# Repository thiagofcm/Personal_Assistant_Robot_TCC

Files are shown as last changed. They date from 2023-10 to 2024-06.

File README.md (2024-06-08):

# Personal Assistant Robot - Bachelor's Thesis

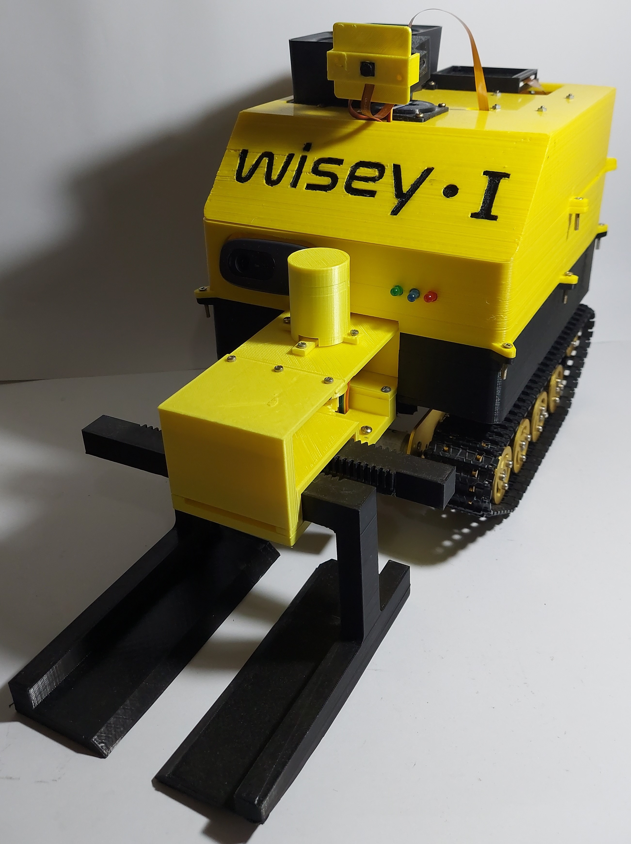
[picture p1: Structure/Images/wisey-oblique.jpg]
robot-oblique


# 1. Objective 
The main goal of this work is the development of an assistive robotic system capable of serving as an alternative for the care of elderly individuals with motor limitations. The robot will feature hardware and software resources related to artificial intelligence and computer vision applications to navigate through a domestic environment. Through voice commands, it will perform three tasks: recognize and deliver objects (Finder Mode), provide information and interact with users (Conversation Mode), and follow individuals (Follow Mode).

# 2. Methods

# 2.1 Development of MCUs firmwares:
- Development of Raspberry Pi 3 firmware, involving speech recognition and serial communication to send commands to the Maixduino MCU.
- Development of Maixduino firmware responsible for object and face detection, and reception of commands and data from the Raspberry Pi.
- Development of STM32 firmware, responsible for controlling motors and the ultrasonic sensor, as well as receiving commands and data from the Maixduino MCU.

# 2.2 Development of a PCB:
A professional PCB was designed on KiCad to ensure robust hardware-level functionality

# 2.3 Development of a robust structure:
- The robot's structure consists of a rover track belt connected to each motor, an aluminum chassis, and an external 3D structure.

# 3. Results

# 3.1 Software Design: 
Internally, the robot's functionallity is based on 3 embedded firmwares in 3 MCUs: 

- Raspberry Pi 3: This firmware responsible for Wi-Fi connectivity, processing audio data via the Google Speech-to-Text API, and transmitting data via UART to the Maixduino MCU. Basically, the Raspberry Pi will listen to voice commands and look for specific keywords, like "follow" or "bring me". Depending on which word/expression was detected, the Raspberry will send a UART message to Maixduino defining which AI it has to run
- Maixduino Sipeed: This MCU houses the neural network, camera, and embedded machine learning models. More especifically, this Maixduino's firmware runs AI models for object and face recognition under UART commands from the Raspberry Pi, and transmit targets coordinates to a STM32 MCU. 
- STM32F41106CCEU6:  This MCU is in charge of receive UART data from the Maixduino MCU and apply PWM signals to control the robot's position. The SMT32's firmware also controls an ultrassonic sensor and a buzzer that is enable when an obstacle is detected under 20cm

The image below shows a diagram illustrating the functionality, peripherals, and the relationship established between the MCUs.

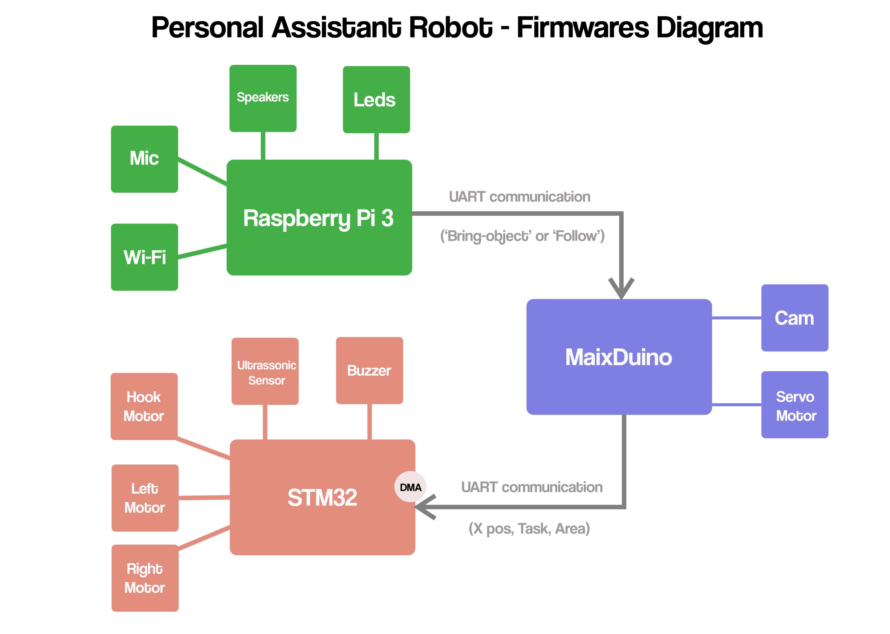
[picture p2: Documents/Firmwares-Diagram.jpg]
SOFTWARE_DESIGN


# 3.2 PCB Development: 
A Printed Circuit Board (PCB) compatible with all the hardware resources used in the system, from MCUs to sensors, motors, LEDs, etc., was designed using the KiCad software. After being designed, the board was manufactured by JLC PCB. Below are images of the board layers as well as the board already fabricated and assembled. The files for reproduction and more information about this part of the project can be found in the PCB folder.

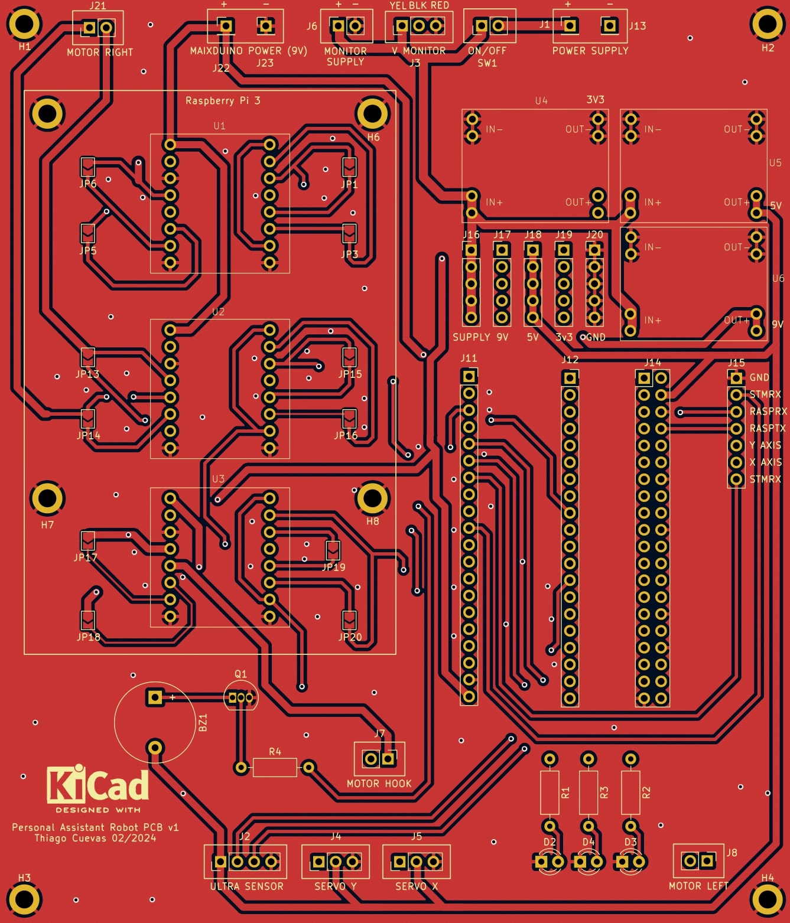
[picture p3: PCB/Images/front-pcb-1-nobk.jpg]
PCB_FRONT

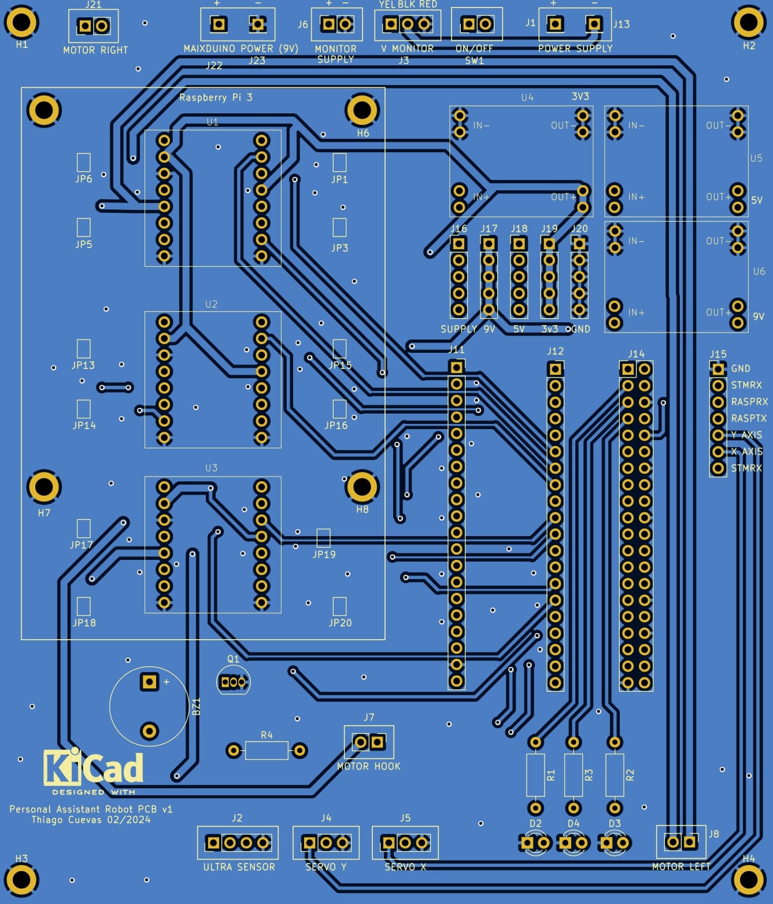
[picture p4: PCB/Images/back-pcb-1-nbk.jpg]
PCB_BACK

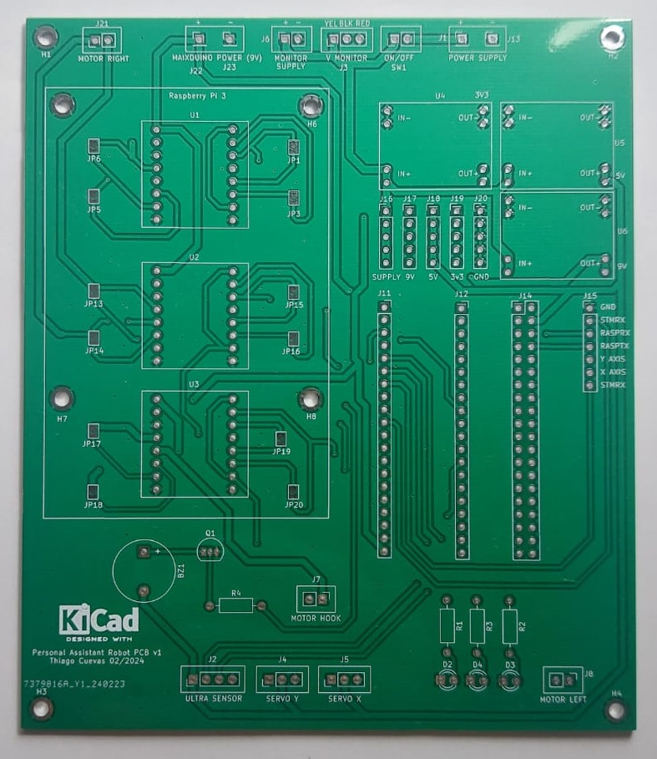
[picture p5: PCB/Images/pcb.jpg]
PCB_MANUFACTURED

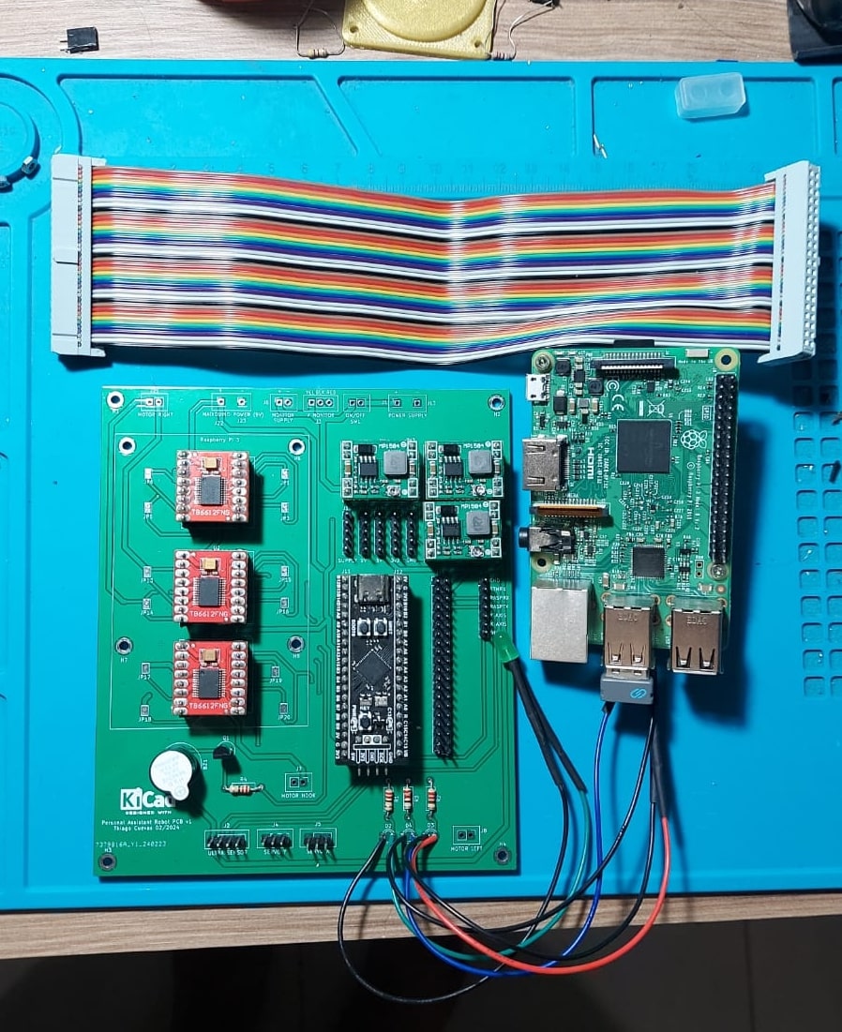
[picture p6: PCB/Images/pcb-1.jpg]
PCB_MOUNTED_1

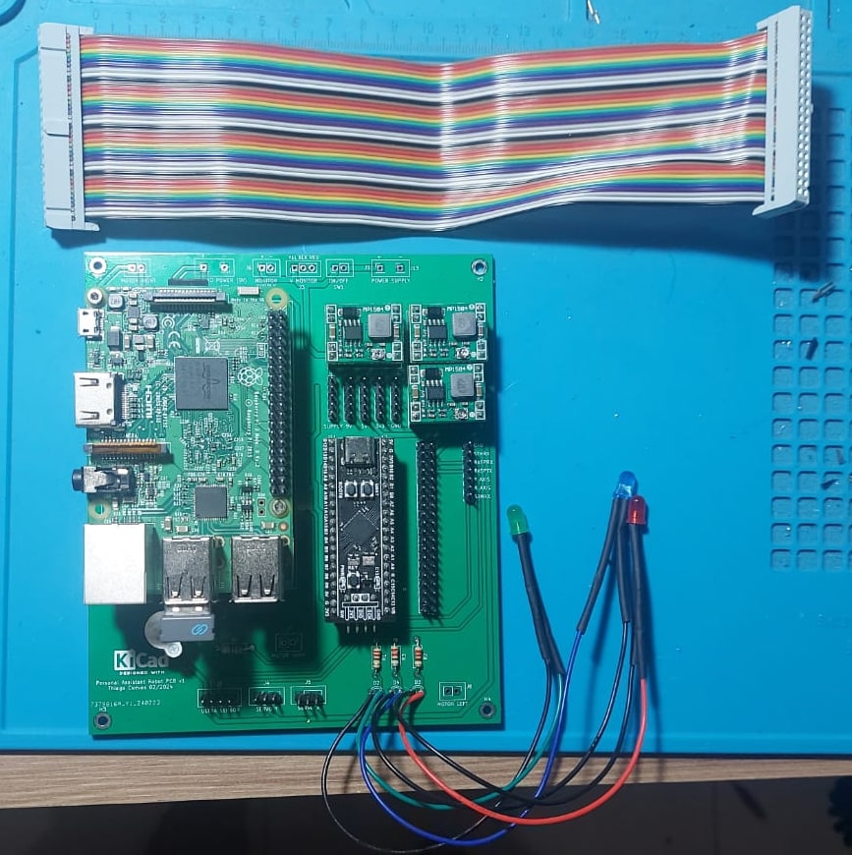
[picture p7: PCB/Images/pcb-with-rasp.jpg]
PCB_MOUNTED_2


# 3.3 Structure Design
A modular structure was designed using the 3D modeling software Fusion 360 and was subsequently manufactured using 3D printing technology. All parts were designed to be compatible with the physical components of the system, as well as adapted to enhance the system's performance. The .SLT, .F3D files, and more images can be found in the Structure folder.

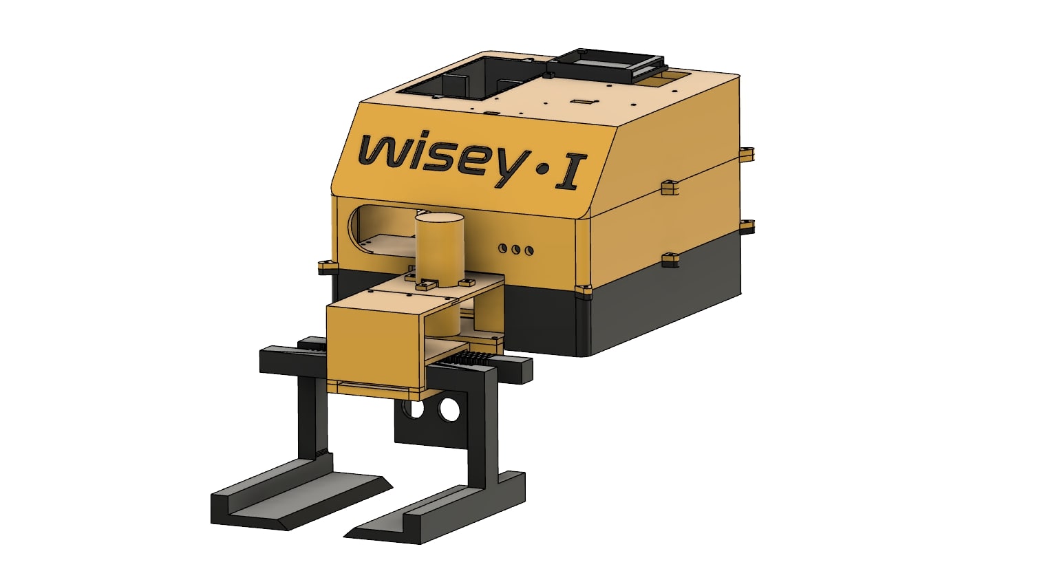
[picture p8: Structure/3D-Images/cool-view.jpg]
3D-VIEW

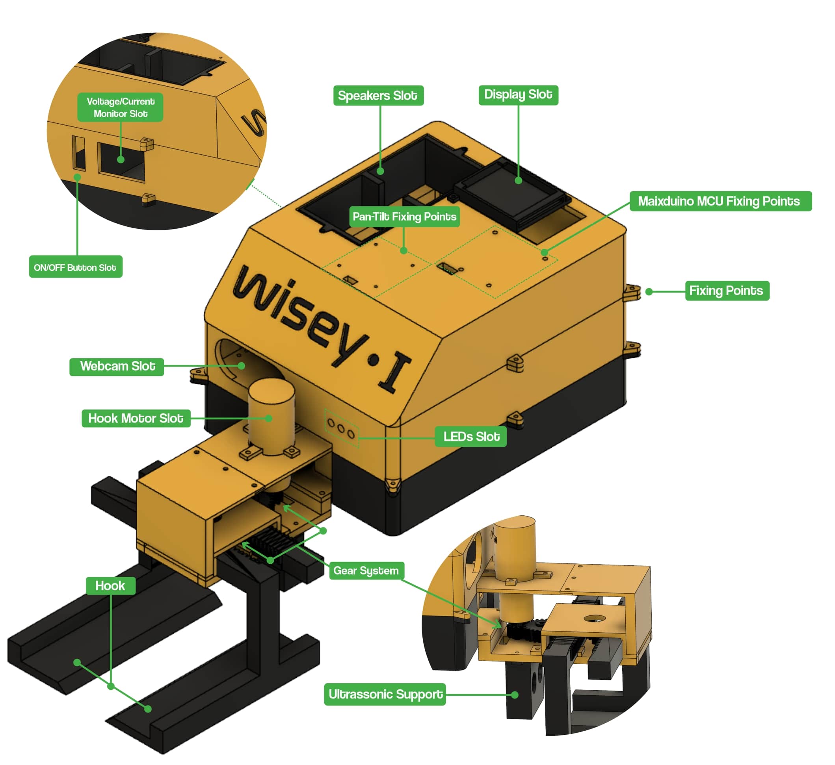
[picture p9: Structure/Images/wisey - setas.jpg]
3D-VIEW_WITH_SETAS


# 4. Robot Images:
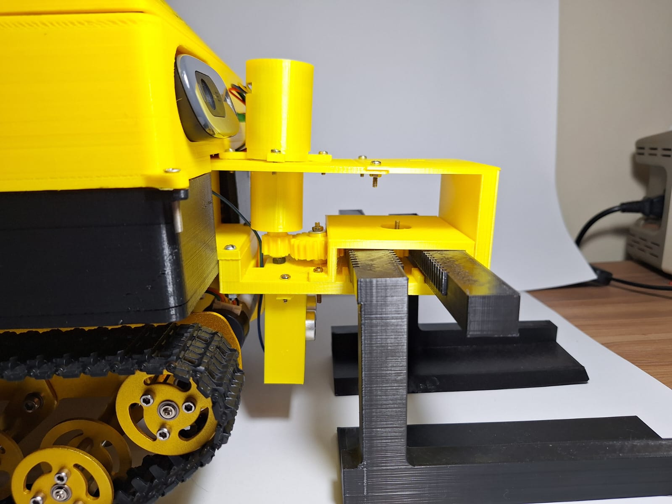
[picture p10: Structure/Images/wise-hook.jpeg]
Personal_Assistant_Robot1


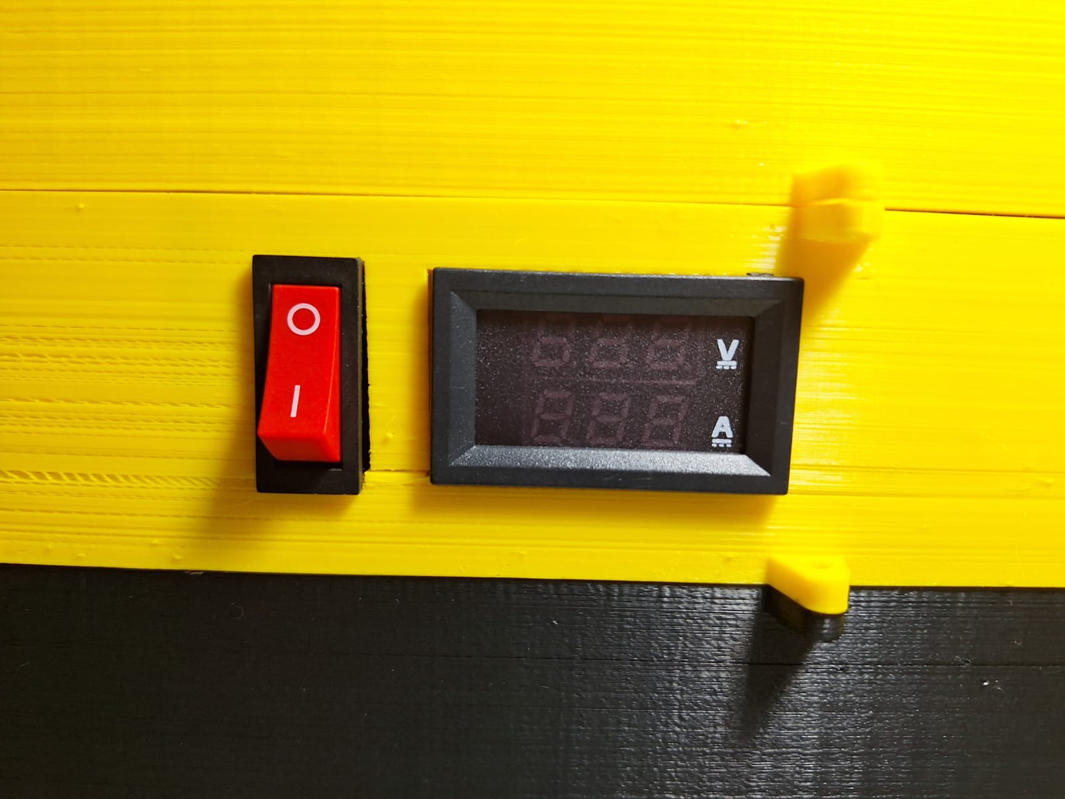
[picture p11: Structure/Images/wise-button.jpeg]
Personal_Assistant_Robot2


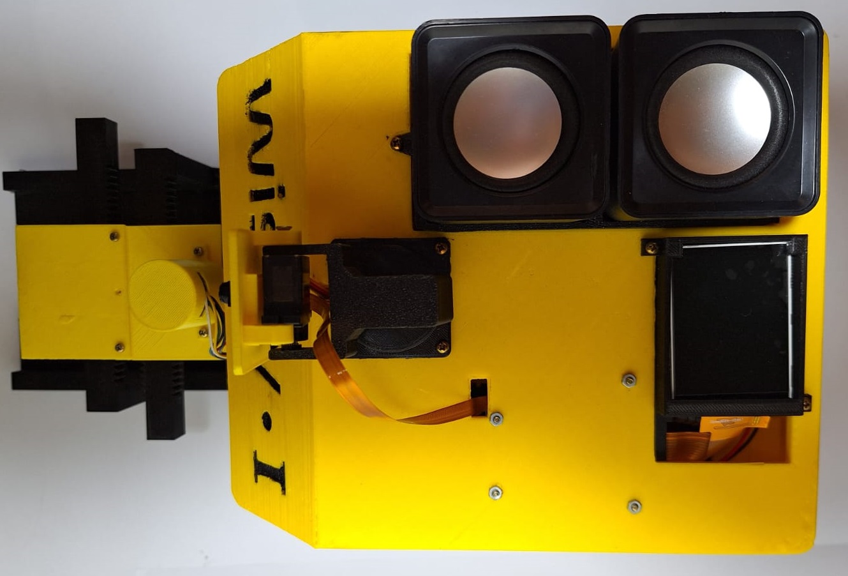
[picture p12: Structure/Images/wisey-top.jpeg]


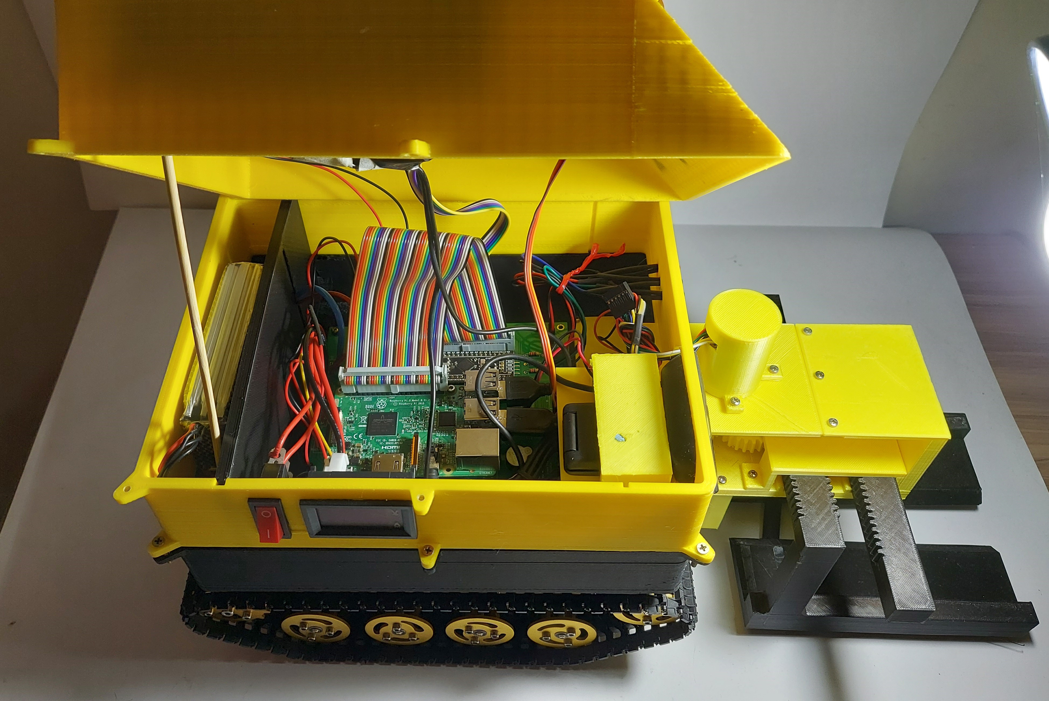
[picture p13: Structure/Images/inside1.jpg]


In the Development Checkpoints folder, you can find the entire development process of the project, including problems, solutions, challenges, tests, failures, and successes. I found it important to document this entire process so that if anyone is interested in reproducing and improving the project, they have references.

# 5. Functionallity

The images below ilustrate the current funcionality of the robot:

Follow Mode:

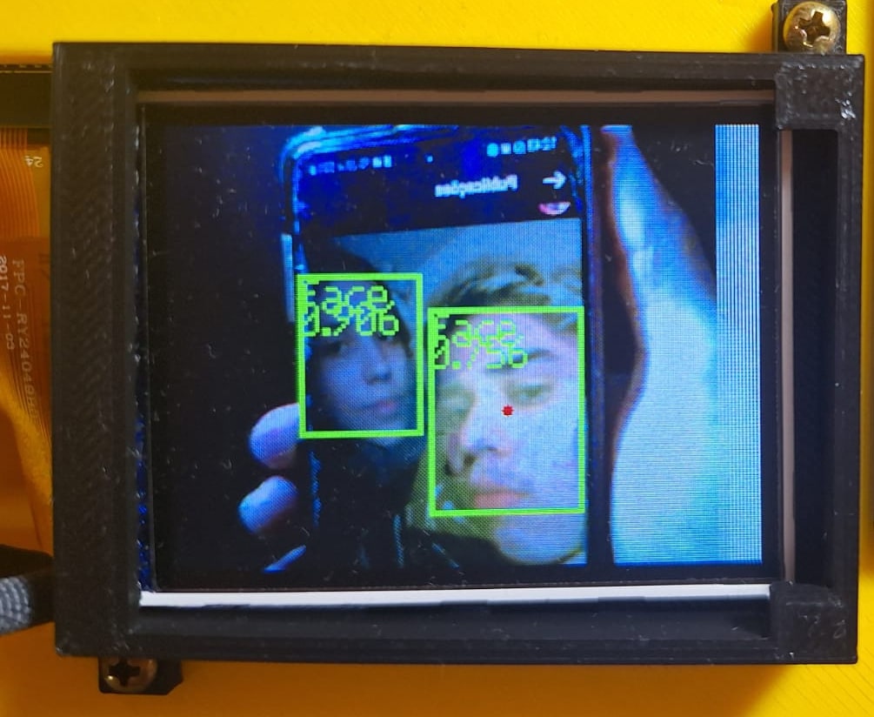
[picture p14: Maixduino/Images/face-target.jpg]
face_target


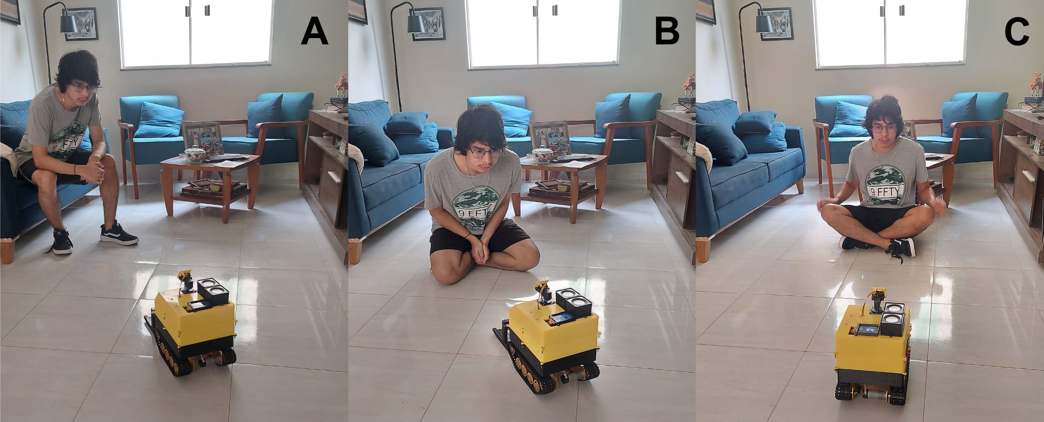
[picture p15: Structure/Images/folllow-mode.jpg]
follow-test


Finder Mode:
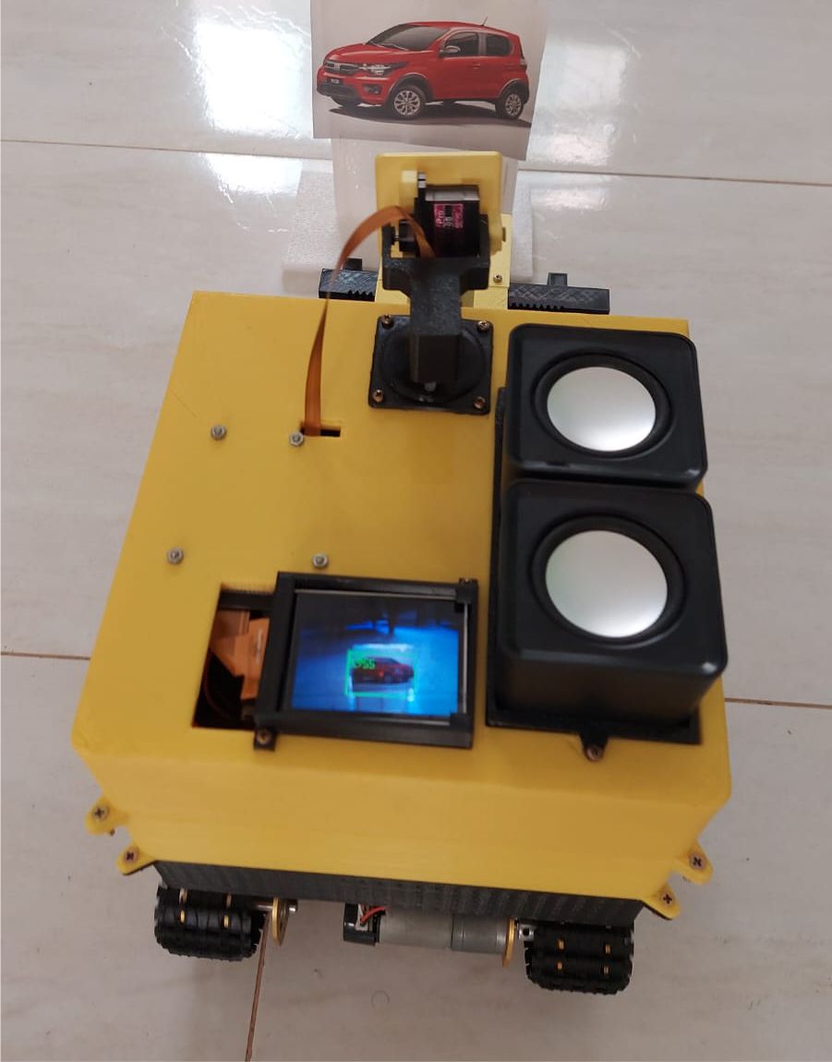
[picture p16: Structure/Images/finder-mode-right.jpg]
finder-test-right


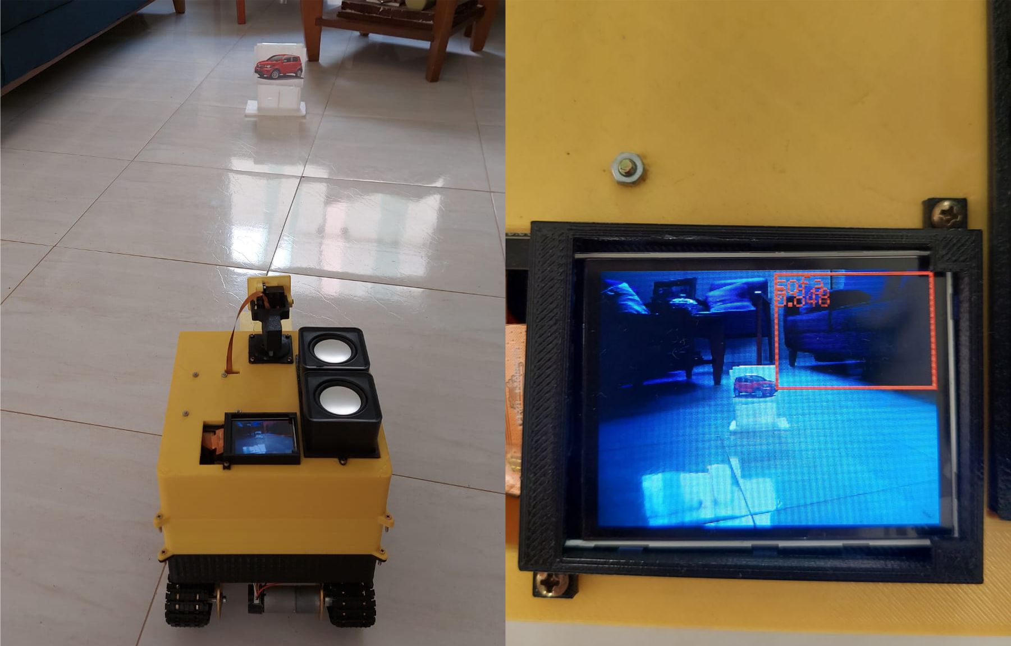
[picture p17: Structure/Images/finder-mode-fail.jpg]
finder-test-fail


# 6. Demonstration Video:

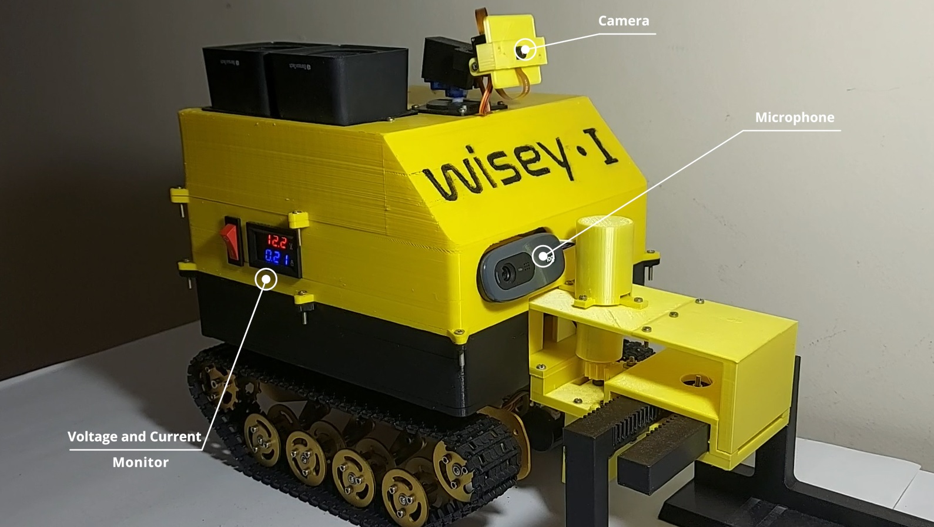
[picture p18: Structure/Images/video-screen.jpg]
video-screen


A demonstration video of the robot in operation is available at the following link: https://youtu.be/cWnuLTotcqo?si=knrNkCdaKpj5jtFy

# 7. References
The robot is a rover based on the project below:
https://github.com/SaralTayal123/Object-Finding-Rover/tree/master

Contact:
Email: thiagof1503@gmail.com
Linkedin: https://www.linkedin.com/in/thiago-cuevas/

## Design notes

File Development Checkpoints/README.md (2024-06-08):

# Updates and checkpoints:

01/08/23: Basic Hardware and Software Tests Stage - Motor Control tests.

11/08/23: Basic Hardware and Software Tests Stage - Ultrasonic sensor tests.

20/08/23: Basic Hardware and Software Tests Stage - Motor Control and Ultrasonic sensor Integration.

02/09/23: Basic Hardware and Software Tests Stage - Temporary PCB added to the circuit.

01/10/23: Basic Hardware and Software Tests Stage - The robot is now capable of moving through the environment and avoiding obstacles using the ultrasonic sensor. 

20/12/23: Writing and formalization of the preliminary project to be submitted to the evaluation committee of the Electrical and Computer Engineering Department.

07/01/24: Finish of the preliminary project (Documents/Projeto__TCC__Thiago_Cuevas.pdf).

12/01/24: Development of the speech recognition and voice assistant firmware on Rasbperry Pi 3 (Rasp/scr). 

16/01/24: Development of a UART communication firmware test between Rasp and Maixduino.

15/01/24: Development of the tracking objects firmware on Maixduino. A servo motor is already capable of follow the movement of an object.

20/01/24: Voice assistant running with an ChatGPT API that answers questions based on OpenAI database.

22/01/24: UART communication between Rasp and Maixduino done and already capable of switch between two different AI models (face recognition, to follow people, and object detection, to deliver objects).

23/01/24: Looking for complete and make improvements in the maixduino switching_models and voice_assistant code. Some problems include:
- The voice assistant still listening during an object or face detection task, which it's annoying because the assistant tries to listen and understand what he is not supposed to listen or understand.
- The Object recognition model needs to track and get the relative position of the object. The code at this point already satisfies this requirement, but without any filter. As the user asks for an especific object, the firmware has to understand and apply an filter to track the right object.
- The Face recognition model needs to track and get the relative position of a face, and also estimate a distance based on the area of the rectangle draw around a recognized face. This feature is not complete.

24/01/24: Looking for make improvements in the IA models. Updates:
- Maixduino is running a Switching models code able to change between the object detection and face detection model by serial commands from the Raspberry Pi.
- Maixduino display a message "waiting command" when it is awaiting for a voice/serial command by the user and the Raspberry Pi.

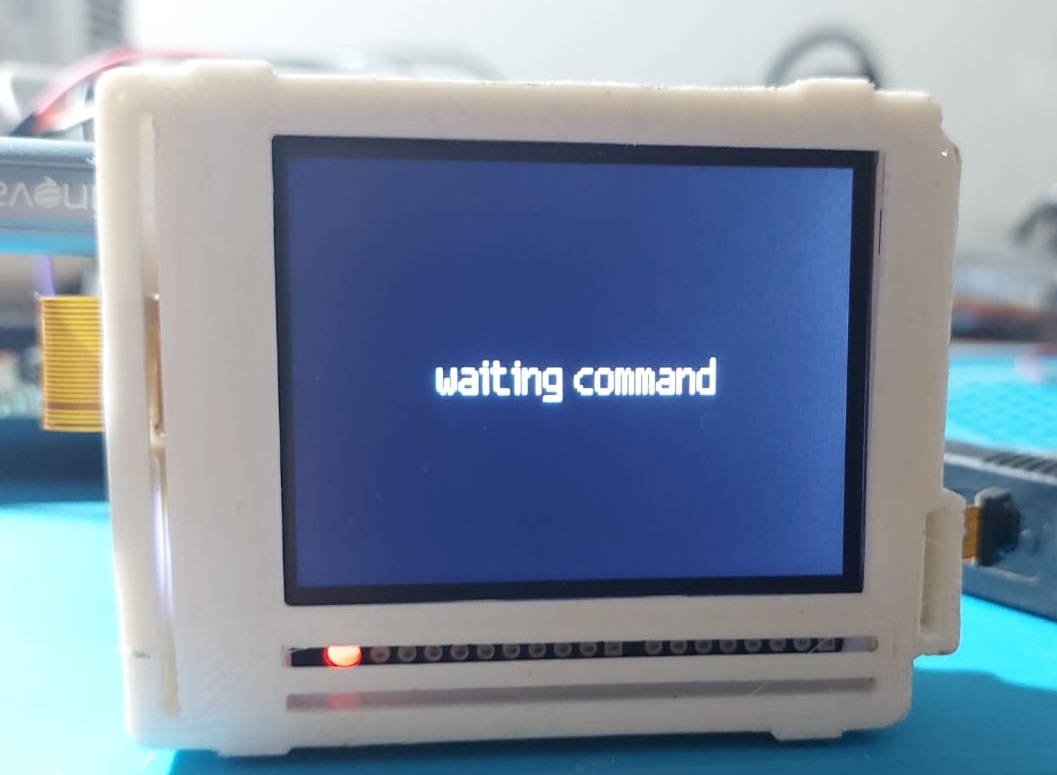
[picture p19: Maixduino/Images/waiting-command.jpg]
image_waiting_command


- Object detection function now gets the relative position only of the objects required by the user. In the example below, the object required was a car, so the rectangle red and the red circle in the center of the object represents that the model understand that is the object that has to be tracked. 

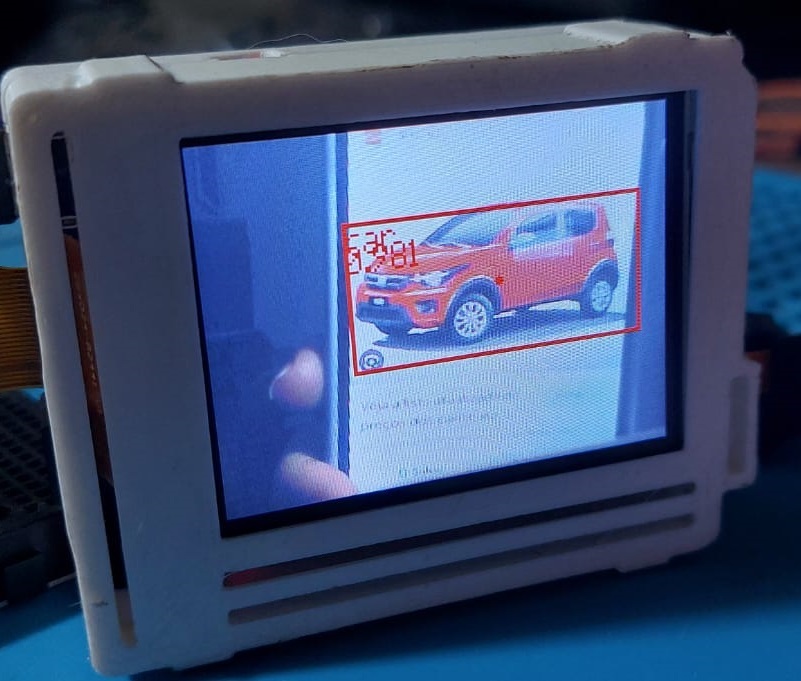
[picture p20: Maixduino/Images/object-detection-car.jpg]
image_car_object_detection


In other hand, the image of a dog, that's not a car is sourrounded by a green rectangle without any circle in the center, representing that despite recognized, the object is not being tracked.

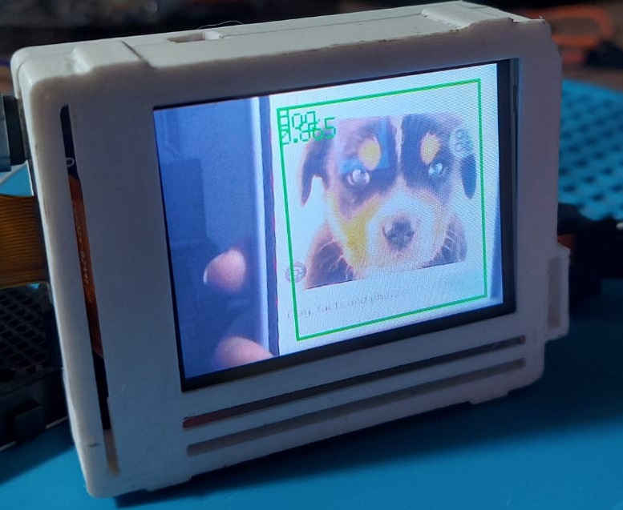
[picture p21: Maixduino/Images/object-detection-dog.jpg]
image_dog_object_detection


- Face detection function now gets the relative position of faces but just one at time. Seems like when more than one face is captured by the camera, the program doesnt know exactly wich face to track. 

25/01/24: Improvements in the Face Detection model done. Updates:
- The Face Detection model is now able to identify the face with largest area and draw a circle in the center of the rectangle area around the face. This circle is used to track de coordinates of the face's position.

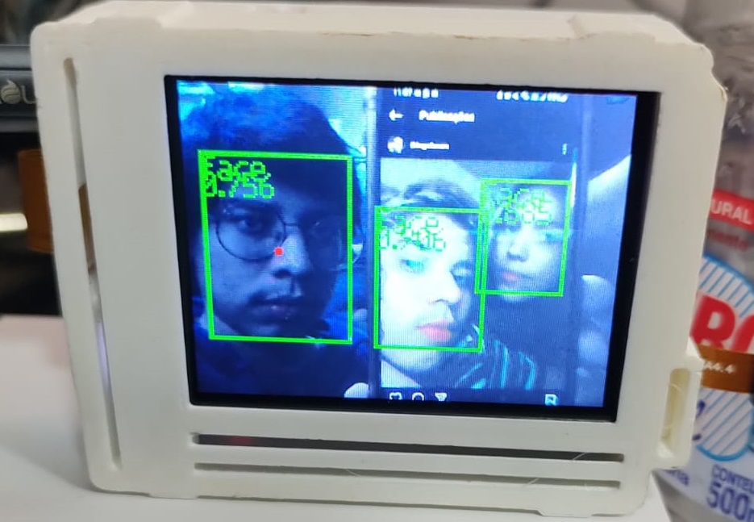
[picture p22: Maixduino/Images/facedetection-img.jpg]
faces_recognition


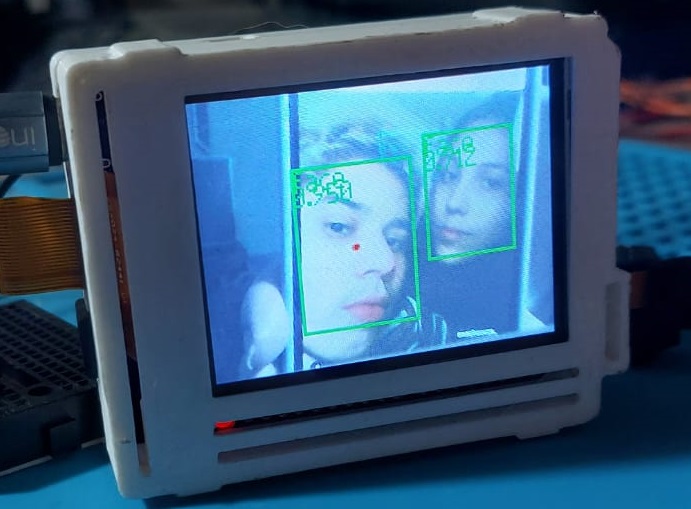
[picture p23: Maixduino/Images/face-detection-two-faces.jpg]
faces_recognition_2


29/01/24: A 3D Pan Tilt has been printed and added to see the servo tracking control. Updates:
- The tilt can follow the face with the biggest area. 
- Face detection firmware now gets the x and y relative position and send it via UART to the STM32 (UART seems to be easier to control than I2C protocol).
- The plan is make the STM32 MCU receive data in the format (x,y,area). I am trying to use the Direct Memory Access (DMA) to receive the data in order to significantly reduce the CPU load. However, I still don't know why, but the STM32 is receveing just one byte of the whole frame data from the Maixduino. Example: If I send (23,53,5432), the STM32 is able to fill one or two positions of the buffer, like '(' and sometimes '(' and '2'. I tested this STM32 firmware trying to receive data from the Raspberry Pi and it worked, but with Maixduino did not.

tracking_faces

01/01/24: The STM32 is now receiving the complete coordinates data from Maixduino, in the format (x,y,area) and using DMA. Updates:
- A new microphone from Logitech Webcam was added. Now, the voice recognition is more accurate and the system can listen commands in a larger distance.

02/02/24: Based on the x coordinate received by the Maixduino, the STM32 is now able to adjusts the PWM signal sent to the motors and make movements like turn to the right, left, and stop ensuring the robot maintains its position consistently in front of the object or face. 
- I still need to add a function to handle the received area data and adjust a threshold parameter to maintain an optimal distance between the object/face and the robot. However, to guarantee accurate modifications and calibrations in this implementation, it is necessary to have an autonomous system and structure already working, one that does not depend on USB supply. 
 
motor-tracking-objects

04/01/24: I developed a block diagram of the system workflow (Documents/Personal_Assistant_Diagram) to facilitate software and hardware design and development.  

07/02/24: I started the schematic of the PCB on KiCad. Software Updates:
- I made some improvements in the ST code. Now the motors stop and a buzzer is activated when an object or obstacle is within a range of 15cm of the robot.
- I added some LEDs to the Rasp Circuit. The green LED turns on when the system is initialized and ready to receive commands. The blue LED turns on when the wake-word is detected, and the red LED represents when the robot is busy on a task.
- These improvements are changes that I had already in mind since the beginning of the implementation, that I was just leaving for the end. However, the PCB design requires that all components and pinouts be counted.

27/02/24: I finished the PCB design on KiCad and have already ordered it on JLCPCB.
- I suppose to receive the PCB by mid or end of march.
- I modeled the 3D Structure on Fusion 360, and now I'm waiting to have all parts printed.

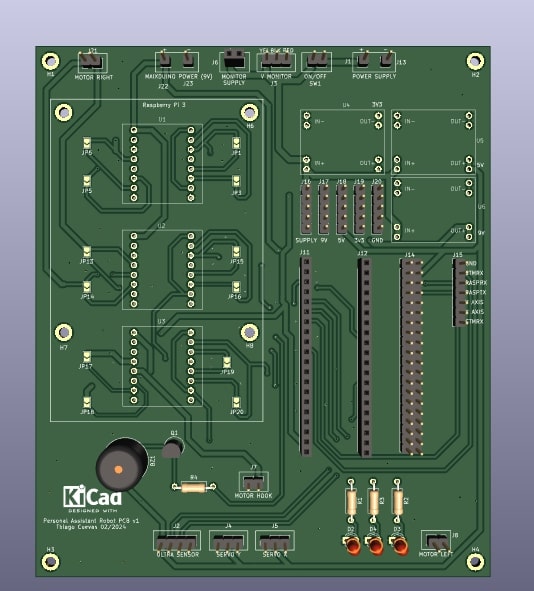
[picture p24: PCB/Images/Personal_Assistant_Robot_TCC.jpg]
PCB


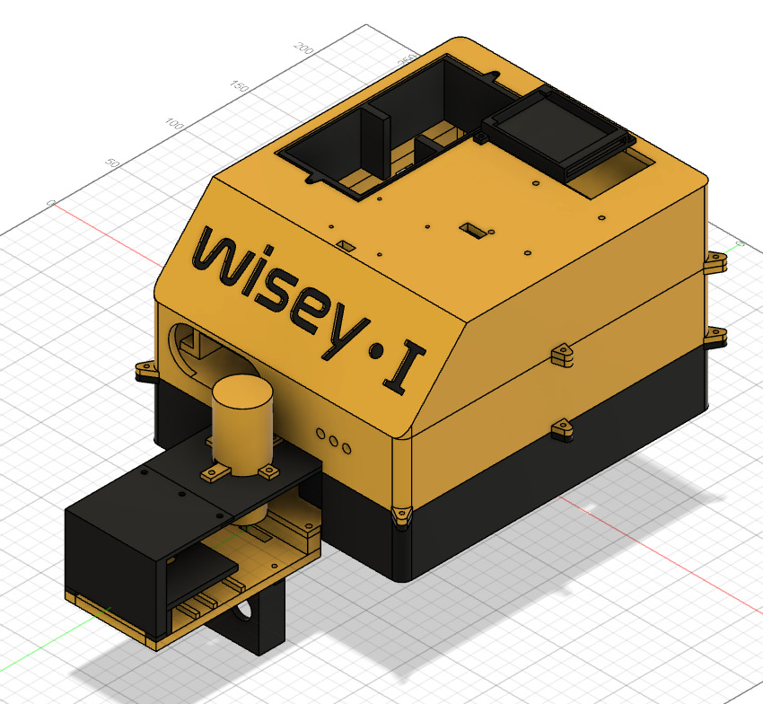
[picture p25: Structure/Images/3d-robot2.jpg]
3D_Structure


20/03/24: After nearly a month of anticipation, both the PCB and the 3D printed structure have finally arrived! :)

pcb-done

- I am currently in the process of soldering the components onto the PCB, meticulously testing each one before integrating them into the entire system. 

pcb-wout-rasp

- The 3D structure fits flawlessly and looks quite impressive.

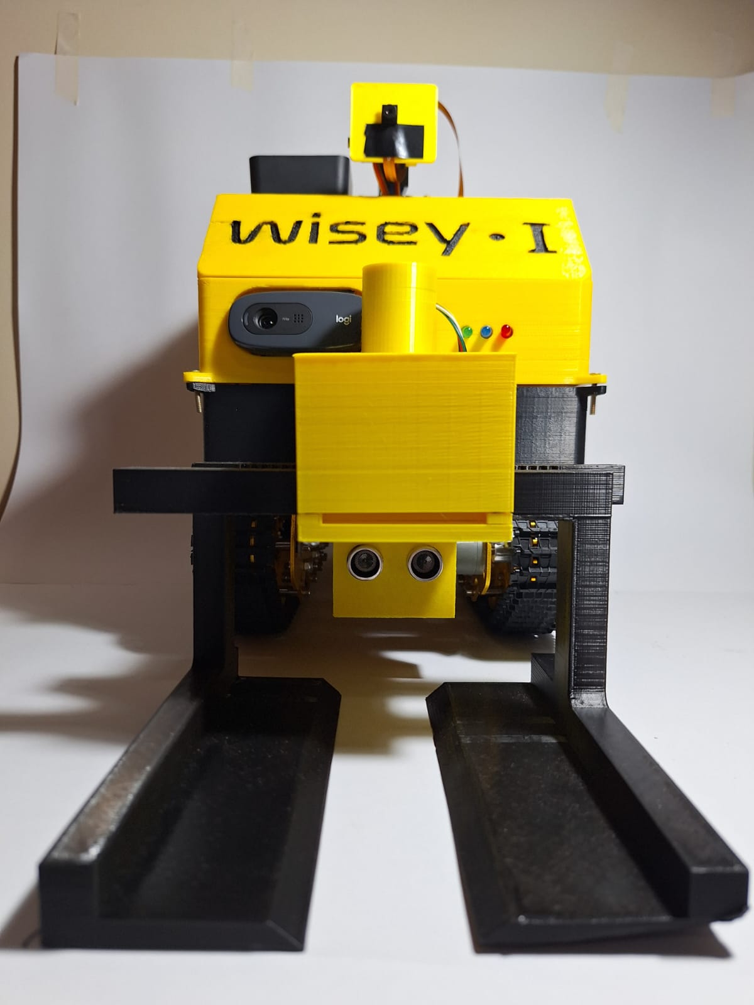
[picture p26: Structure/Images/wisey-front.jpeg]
robot-oblique


- Simultaneously, progress is being made on the written aspect of the project.

12/04/24: The PCB worked very well, and tests to verify the system functionality were conducted. 
- The system successfully interacted with the user, maintaining a fluent and cohesive conversation. 
- The robot also exhibited commendable performance in detecting and tracking users, although it encountered limitations in perceiving and capturing objects.
- Given that the detection model has a restricted list of recognizable objects, with not all of them being domestic items, an adapted structure with a picture of the object was devised to enhance the recognition of specific items.
- It was noted that the model is capable of recognizing objects at close range, possibly due to the camera's low resolution in this dimension.
- Also, the gripper system did not function as expected, likely due to insufficient motor torque and less effective gear system coupling. Despite this, the robot managed to detect objects under specific conditions and move towards them.
- The written part of the project has been done, and after be reviewd by the Faculty, will be available in the Documents directory.
- A video showing all the skills of the robot is under development, and will be available on Youtube.

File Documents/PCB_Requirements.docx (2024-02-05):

Projeto PCB – Personal Assistant Robot

Levantamento de Materiais e Componentes:

- MOTORES:

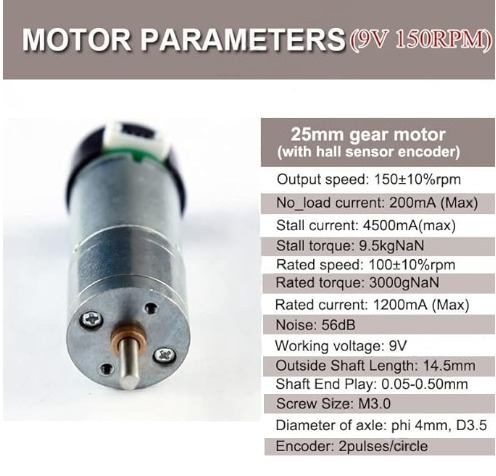
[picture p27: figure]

- Supostamente o motor que estou usando é:

Porém, estou em dúvida pois o modelo de 6V também existe. Medi com o multímetro a tensão que está chegando da ponte H até eles. Considerando a fonte de 12V, a tensão máxima que chega aos motores é de 6,2V. Segundo a imagem acima a corrente nominal é de 1.2A. Como saber qual motor é o meu? E O que aconteceria se alimentar com 3.0A?

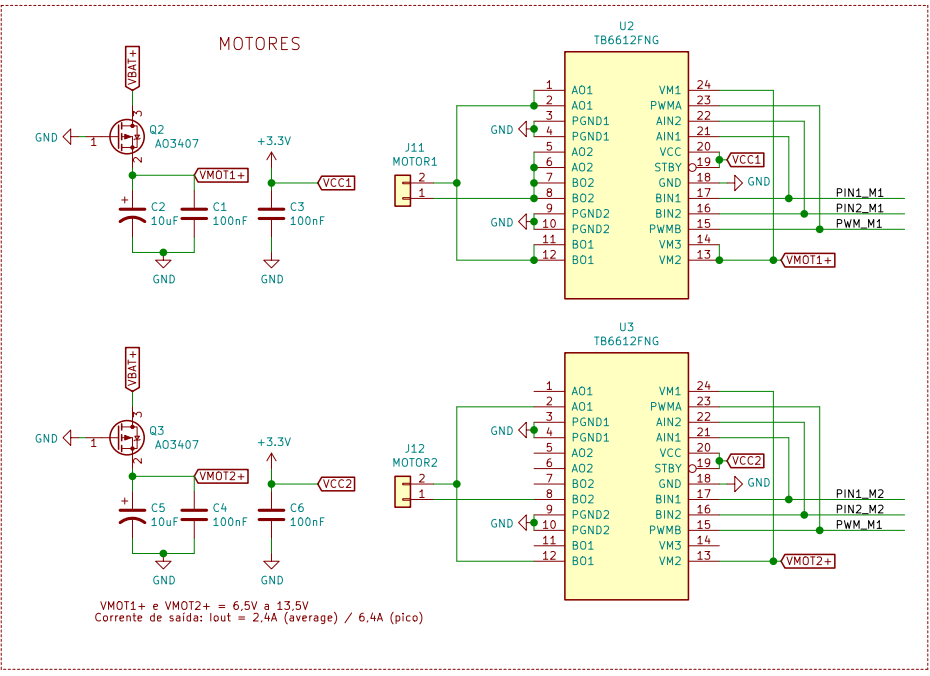
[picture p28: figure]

- Quanto ao controle dos motores, observando o projeto do Lukas, vi que ele usou dois chips TB6612FNG. Cada chip desses possui dois canais para controlar dois motores, mas Lukas usou os dois canais para o mesmo motor. O objetivo foi obter mais corrente para cada um dos motores, uma vez que cada canal fornece até 1,5A, tendo ao final, 3,0A para cada motor.

- A pinagem do TB6612FNG está detalhada no datasheet, é de fácil compreensão. Tenho algumas dúvidas sobre o circuito de alimentação dos motores (VMOT1+ e VMOT2+).

- REGULADORES DE TENSÃO:

A tensão que chega das baterias deve ser regulada para a operação de outros componentes que funcionam com tensão menor. Dessa forma, são necessárias tensões na placa de 6 a 12V, 5V e 3V3.

- Componentes alimentados por 6 as 12V:

x1 Maixduino MCU (via DC Connector)

- Componentes alimentados por 5V:

x1 Servo motor para controle do posicionamento da câmera no eixo Y.

x1 Sensor Ultrassônico.

x1 Raspberry PI 3 (pinos)

x1 Motor DC para controlar HOOK

- Componentes alimentados por 3v3:

x1 STM32F411CEU6

x3 LED’s

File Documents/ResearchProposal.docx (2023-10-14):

Proposta de Trabalho de Conclusão de Curso – Thiago Fernando Cuevas Mestanza

Título: Robô Assistente Pessoal Inteligente

Objetivo: Construir um robô assistente pessoal inteligente capaz de receber comandos por voz e executar tarefas simples como: seguir uma determinada pessoa (Follow Mode), trazer objetos (Find object Mode) e dar informações* (Info Mode)

Assuntos abrangidos: Robótica, Computação Visual, Machine Learning, Eletrônica, Sistemas Embarcados.

Referência direta:

https://www.instructables.com/Object-Finding-Personal-Assistant-Robot-Ft-Raspber/

https://github.com/SaralTayal123/Object-Finding-Rover/tree/master

https://youtu.be/aso3N4YiCAQ

Analise inicial de requisitos, o robô deve possuir:

- Uma estrutura similar a um chassi de carro – TANK SN2500

- Computador – Raspberry PI 3

- Motor Driver – MCU STM32

- Dispositivo com Rede Neural/ Machine Learning Embarcado – Kendryte K210

- Webcam c microfone- xxxxxxxx

- Sensor Ultrassônico - HC SR04

- Acabamento em impressão 3D

- Wi-Fi Driver – MCU ESP32*

- Saída de áudio*

Funcionamento:

A Raspberry PI 3 gerenciaria todas as atividades realizadas pelo robô, sendo ela a responsável por enviar as informações necessárias para os demais drivers e dispositivos, como a STM32, Sipeed e ESP32. Essa segmentação de atividades não sobrecarrega a capacidade de processamento da Raspberry, não compromete outras aplicações do computador e desenvolve as habilidades do estudante.

Nessa perspectiva, A STM32 funcionaria apenas como interface/Driver dos motores, enviando e recebendo informações da Rasp via I2C,RS-232 ou SPI.

O intuito é fazer o K210 funcionar da mesma forma, como uma rede neural a parte, encarregada de fazer o reconhecimento facial e de objetos por Machine Learning, interpretando a imagem obtida pela câmera, além de ser o sistema receptor de comandos de voz.

O Sensor Ultrassônico serviria como um medidor de distância, sendo utilizado somente quando acionado o modo “Find object”. Após um objeto ser encontrado, é ele que mede a distância ideal para acionar o sistema de garras e manter o objeto preso ao robô.

A ESP32 funcionaria como um modulo Wi-Fi capaz de gerenciar o trafego de informações e manter o robô conectado à internet e consequentemente disponível para dar informações sobre clima, localização, data e hora ao usuário através de uma saída de áudio. *

Bibliotecas necessárias:

Reconhecimento de voz

Reconhecimento facial

Reconhecimento de objetos

Principais dificuldades/duvidas:

Com o uso do Kendryte 210, uma câmera webcam não será mais necessária?

O Kendryte consegue reconhecer comandos de voz além do Wake-Word?

Como fazer a interface do Kendryte com o a Rasp?

Se não usarmos Kendryte, que outra opção temos para processamento de imagem?

Todas as bibliotecas necessárias rodam no mesmo MCU?

Outras Referências:

Tank Chassi SN2500 Guide: https://www.makerbuying.com/18100

Wake-Word K210: https://www.youtube.com/watch?v=zJmjSP2nwj0

Biblioteca SnowBoy para reconhecimento de voz com webcam e rasp: https://pimylifeup.com/raspberry-pi-snowboy/

Controle de Motor DC com Rasp e L298N Driver: https://www.youtube.com/watch?v=2bganVdLg5Q

Rasp e Sensor HCSR04: https://www.youtube.com/watch?v=_7drIUmC8Zo

Getting Started with Rasp: https://projects.raspberrypi.org/en/projects/raspberry-pi-getting-started/

Interface STM32 with Raspberry PI via i2c: https://www.youtube.com/watch?v=8SisMjqqgmc

Forum talk about Interface STM32 with Raspberry PI: https://forums.raspberrypi.com/viewtopic.php?t=213305

Maix BIT – Alternativa: https://blog.arduinoomega.com/maix-bit-embarcado-de-baixo-custo-com-ia/

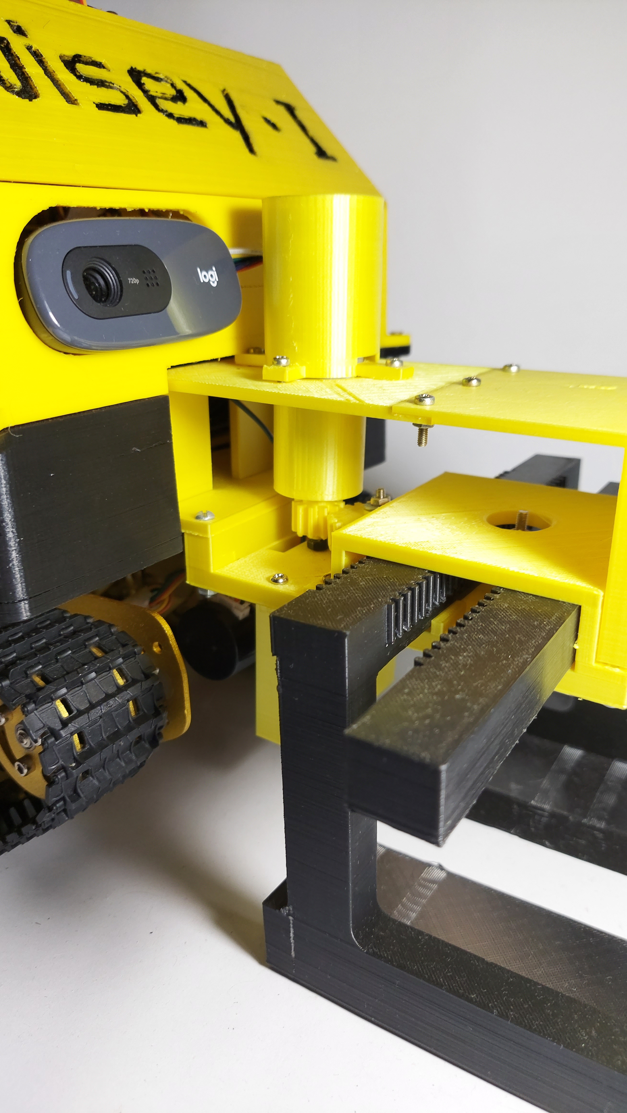
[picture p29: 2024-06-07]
Structure/Images/hook1.jpg

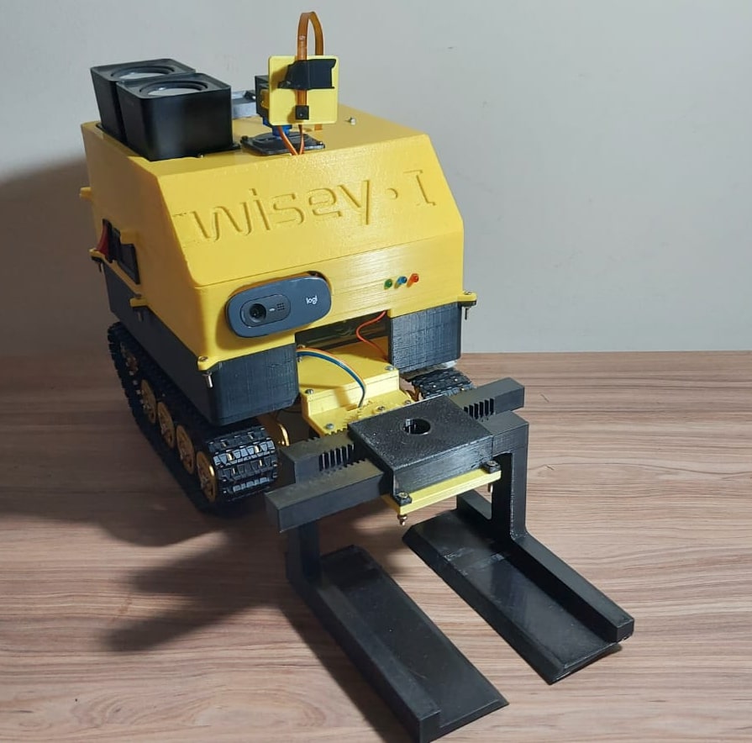
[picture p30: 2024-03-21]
Structure/Images/oblique.jpg

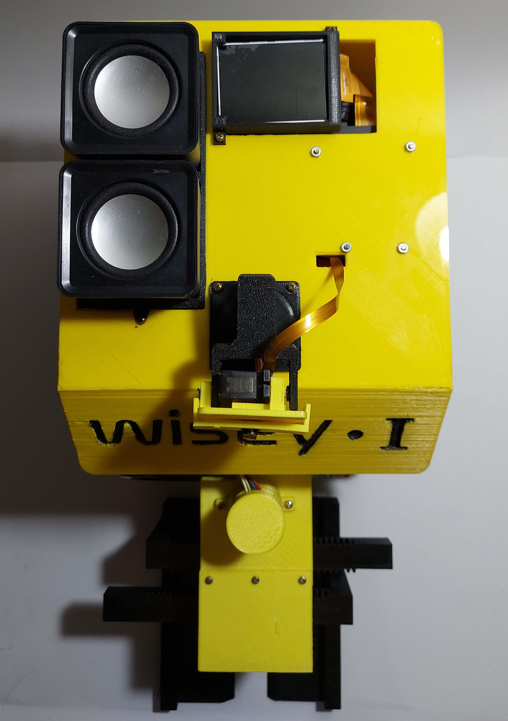
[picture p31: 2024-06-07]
Structure/Images/wisey-topv2.jpg

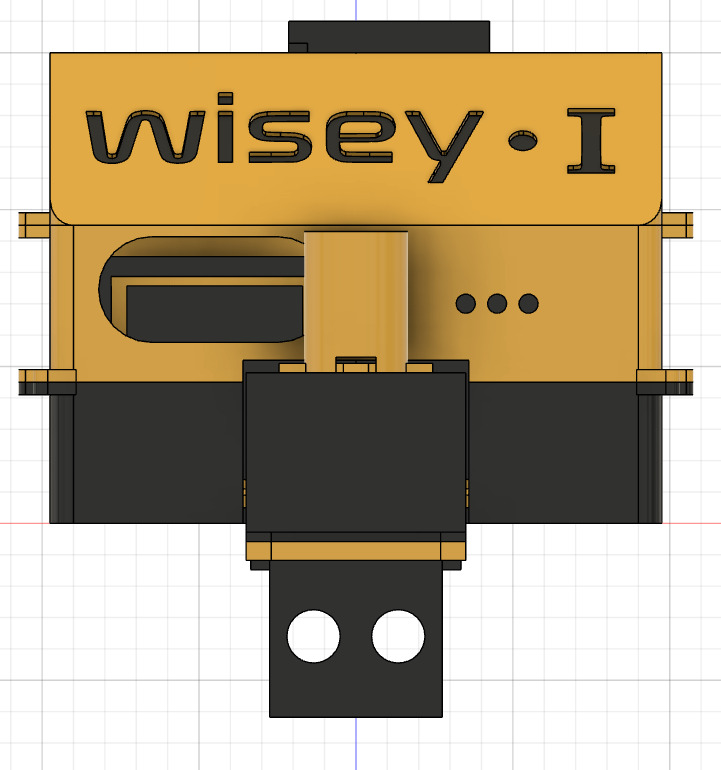
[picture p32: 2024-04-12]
Structure/Images/all+ultrassonic-sensor.jpg

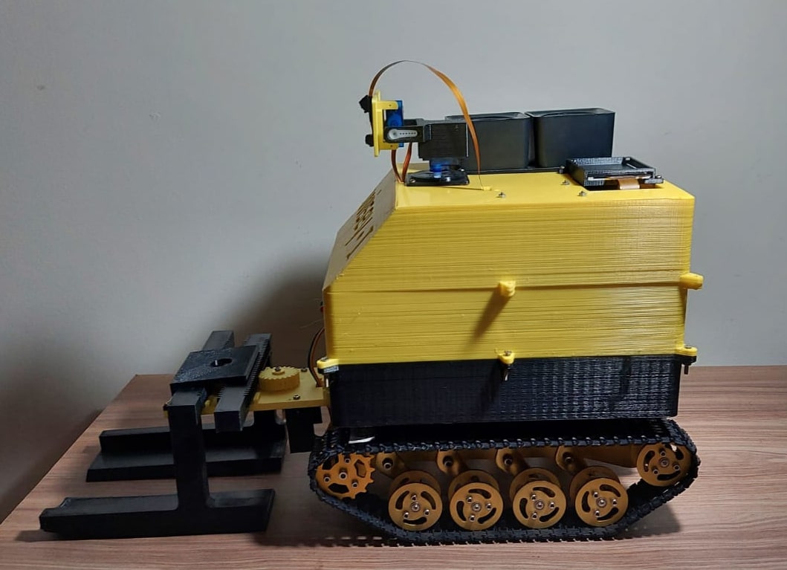
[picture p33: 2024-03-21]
Structure/Images/profile3.jpg

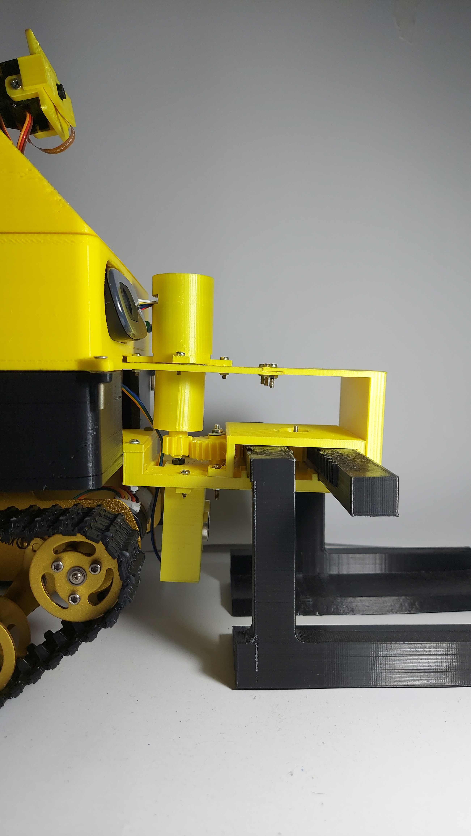
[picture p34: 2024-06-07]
Structure/Images/hook2.jpg

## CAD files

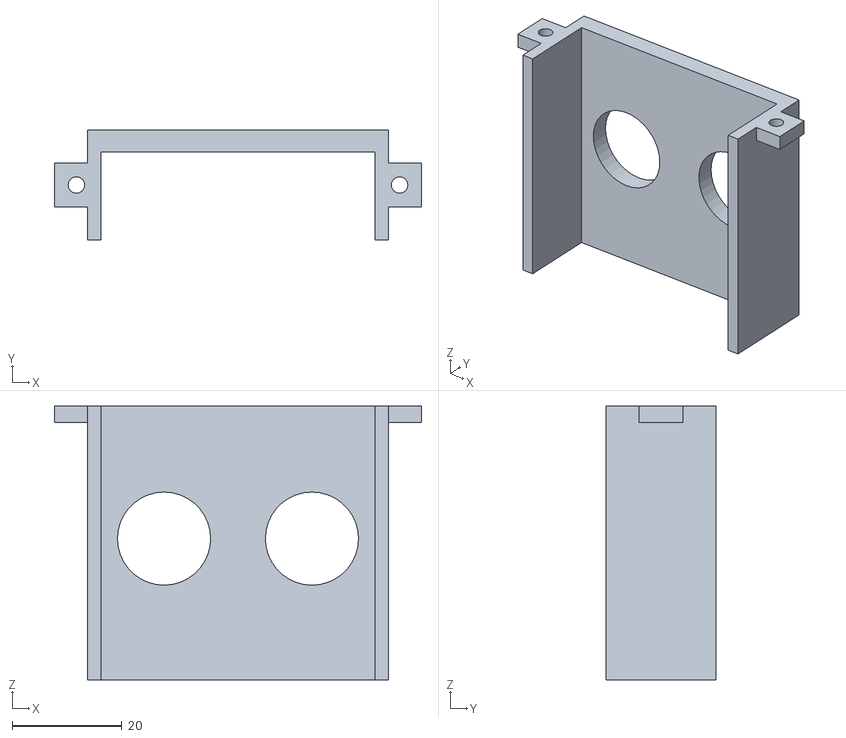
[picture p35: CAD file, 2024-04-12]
Structure/Files/Ultrassonic-Sensor-Support.stl
67.0 x 20.0 x 50.0

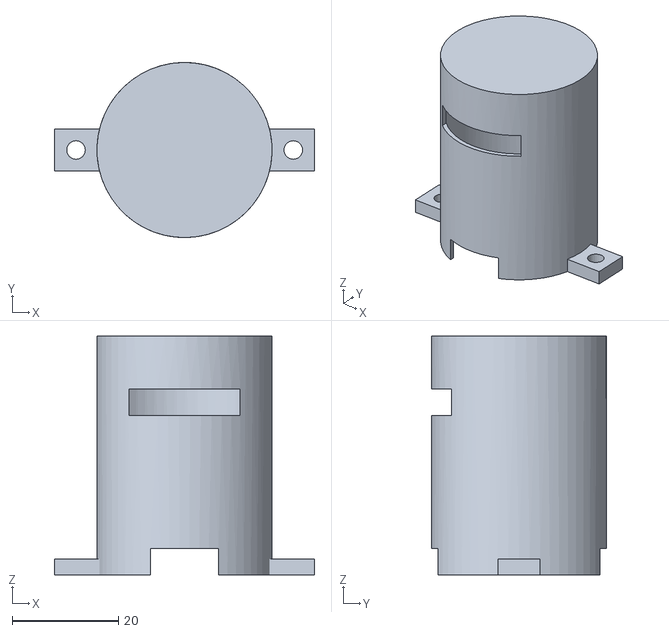
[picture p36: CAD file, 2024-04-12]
Structure/Files/Top-Motor-Hook.stl
49.0 x 33.0 x 45.0

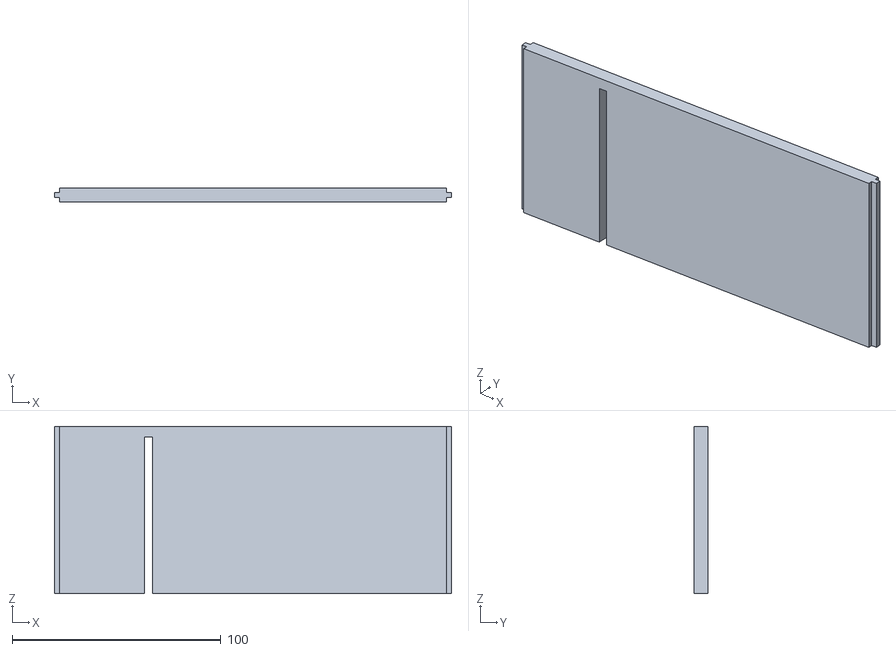
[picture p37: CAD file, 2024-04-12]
Structure/Files/Battery-Division.stl
190.0 x 6.50 x 80.0

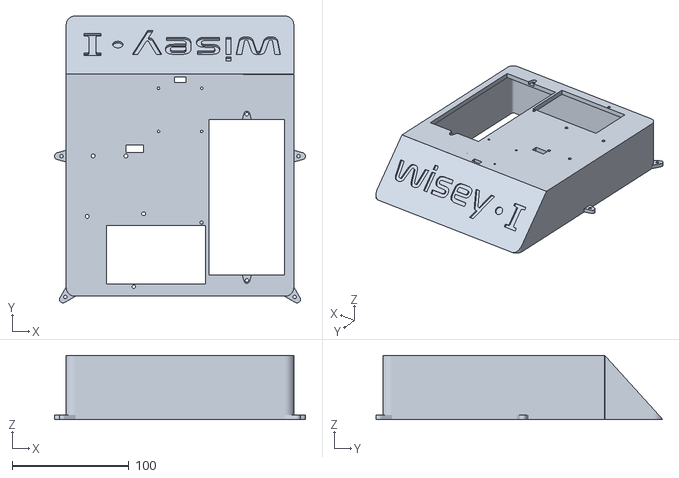
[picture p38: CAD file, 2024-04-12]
Structure/Files/Top.stl
215.0 x 245.8 x 55.0

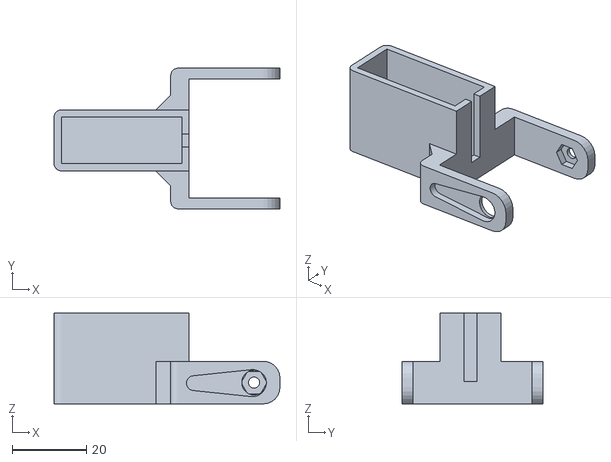
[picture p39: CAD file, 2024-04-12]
Structure/Files/Pan-tilt-tapa.stl
61.0 x 38.0 x 24.5

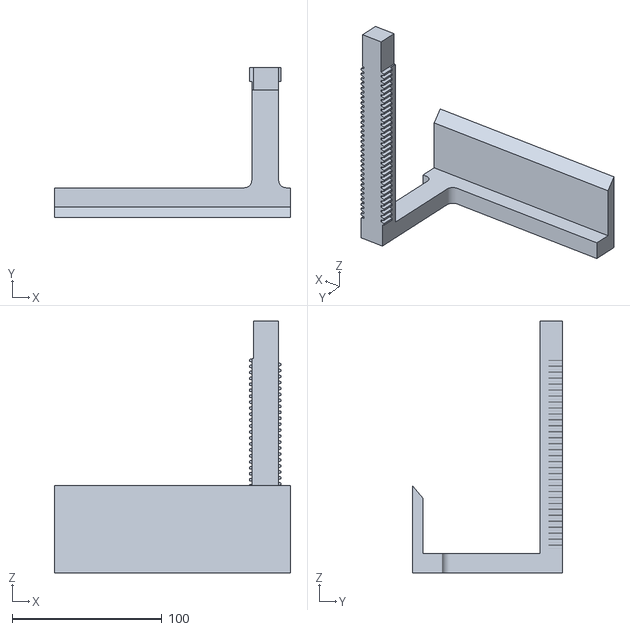
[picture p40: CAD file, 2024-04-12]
Structure/Files/Gear_arm_2_robotic_sled.stl
158.0 x 100.5 x 168.5

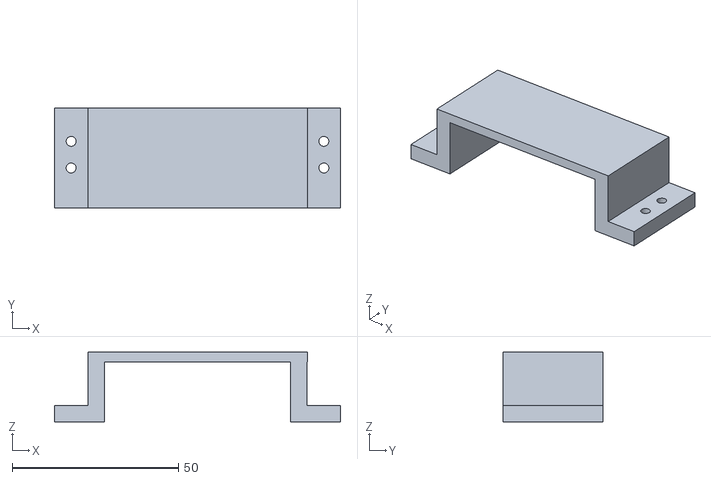
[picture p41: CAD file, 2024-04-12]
Structure/Files/Webcam-Support.stl
86.0 x 30.0 x 21.0

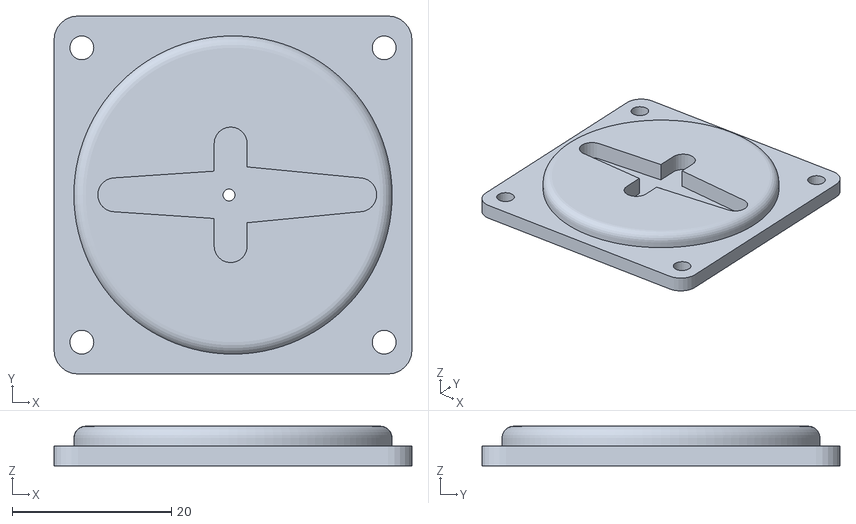
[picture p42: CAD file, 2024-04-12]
Structure/Files/Pan-tilt-plataforma.stl
45.0 x 45.0 x 5.00

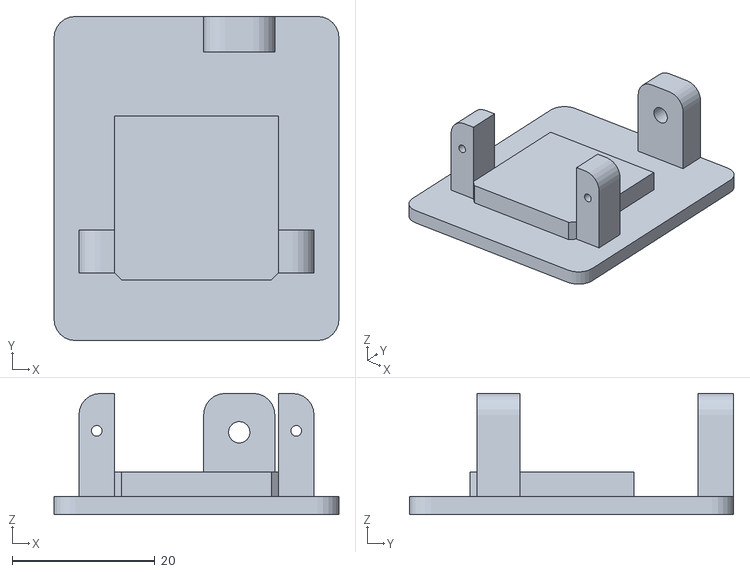
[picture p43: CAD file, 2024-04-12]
Structure/Files/Pan-tilt-base-camara.stl
40.0 x 45.5 x 17.0

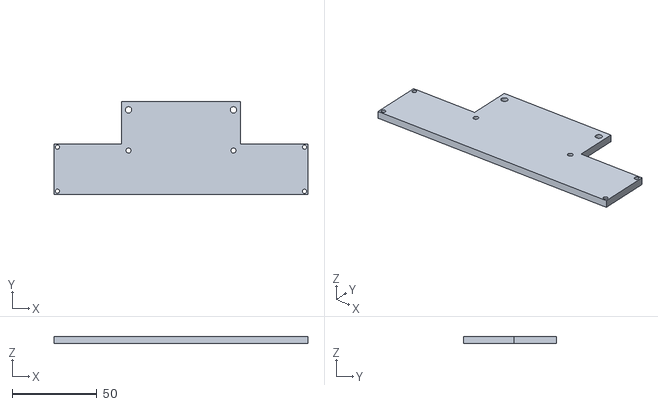
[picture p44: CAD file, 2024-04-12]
Structure/Files/Support-Hook-Support.stl
150.0 x 55.0 x 4.00

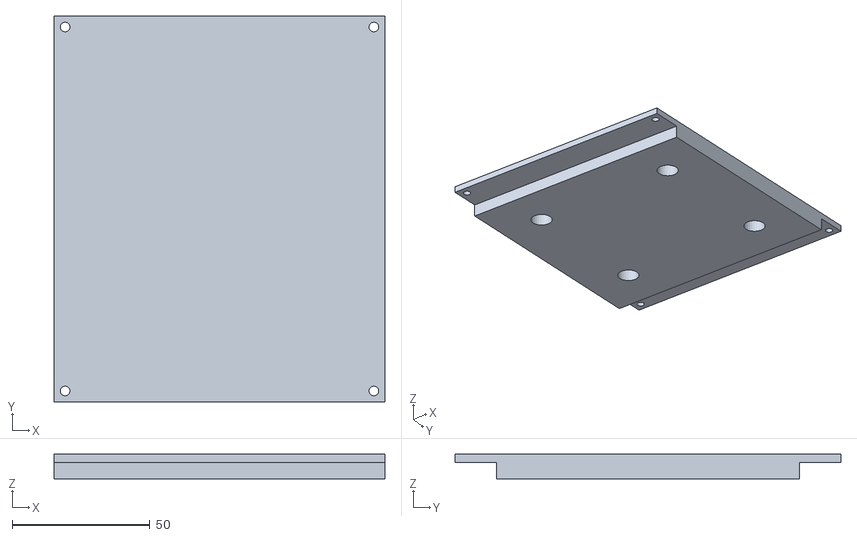
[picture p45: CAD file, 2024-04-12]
Structure/Files/Base-PCB.stl
120.0 x 140.0 x 9.00

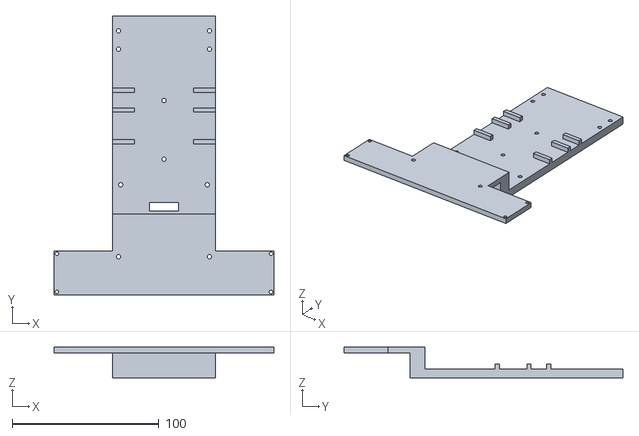
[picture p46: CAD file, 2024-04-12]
Structure/Files/Base-Hook-Support.stl
150.0 x 190.0 x 20.8

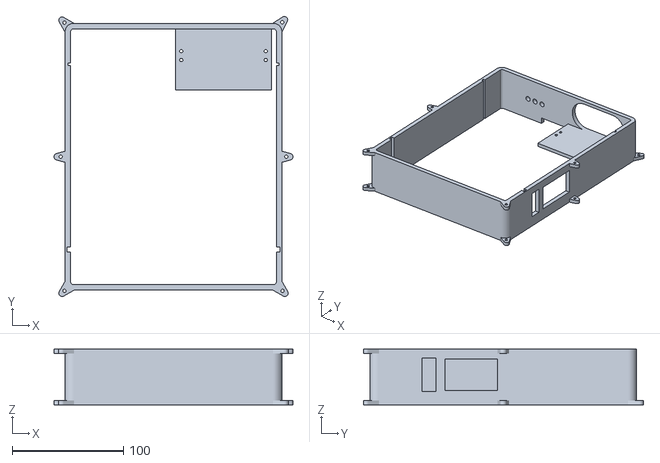
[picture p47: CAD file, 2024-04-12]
Structure/Files/Mid.stl
215.0 x 251.9 x 50.0

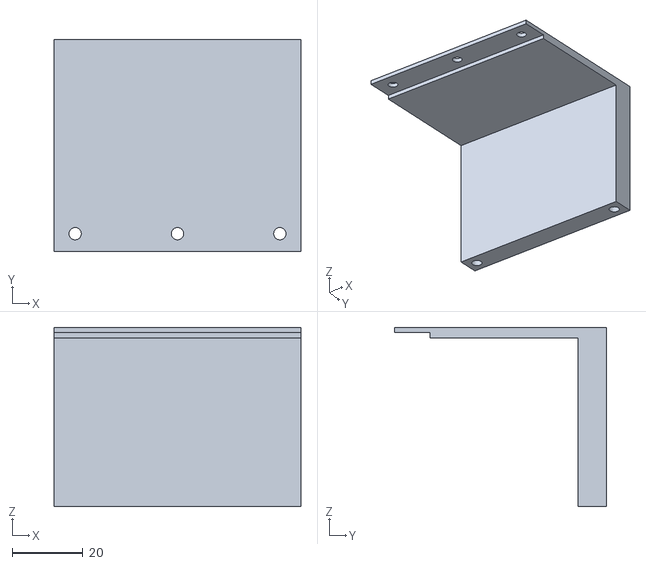
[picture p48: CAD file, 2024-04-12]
Structure/Files/1st-Half-Hook-Support.stl
70.0 x 60.0 x 50.8

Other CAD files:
Structure/Files/Gear_arm_1_robotic_sled.stl
Structure/Files/Base.stl
Structure/Files/2nd-Half-Hook-Support.stl
Structure/Files/Display-Support.stl
Structure/Files/Base-Motor-Hook.stl
Structure/Files/Hook-Support.stl
Structure/Files/Personal_Assistant_Robot_TCC.f3d
Structure/Files/Speakers.stl

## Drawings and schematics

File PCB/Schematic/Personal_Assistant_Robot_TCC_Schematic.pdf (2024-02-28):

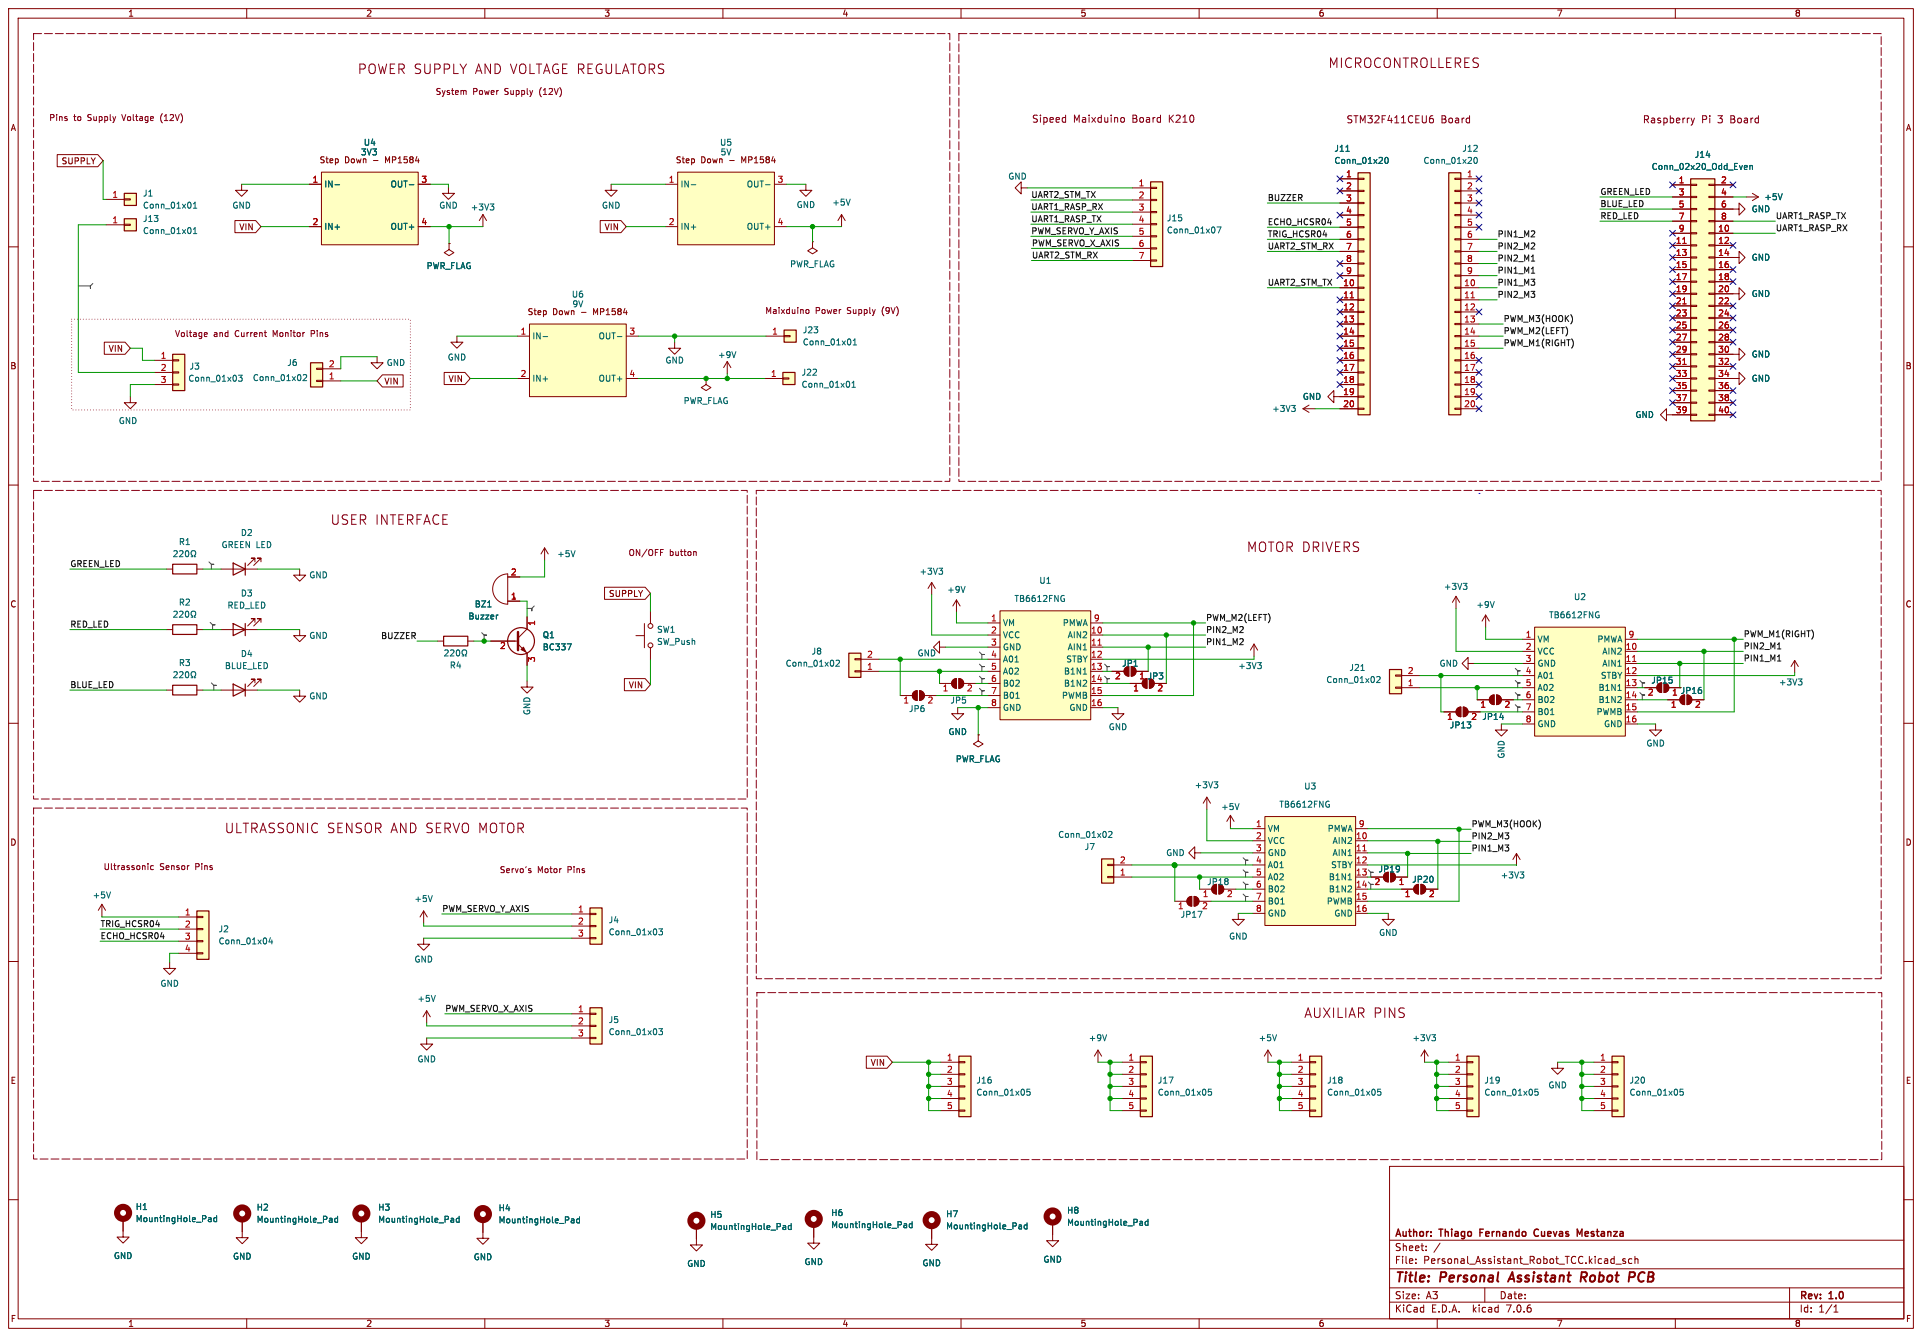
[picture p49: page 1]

POWER SUPPLY AND VOLTAGE REGULATORS

Pins to Supply Voltage (12V)

Voltage and Current Monitor Pins ULTRASSONIC SENSOR AND SERVO MOTOR

Id: 1/1 Title: Personal Assistant Robot PCB

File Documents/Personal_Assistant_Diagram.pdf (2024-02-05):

# Working Flow Diagram - Personal Assistant Robot

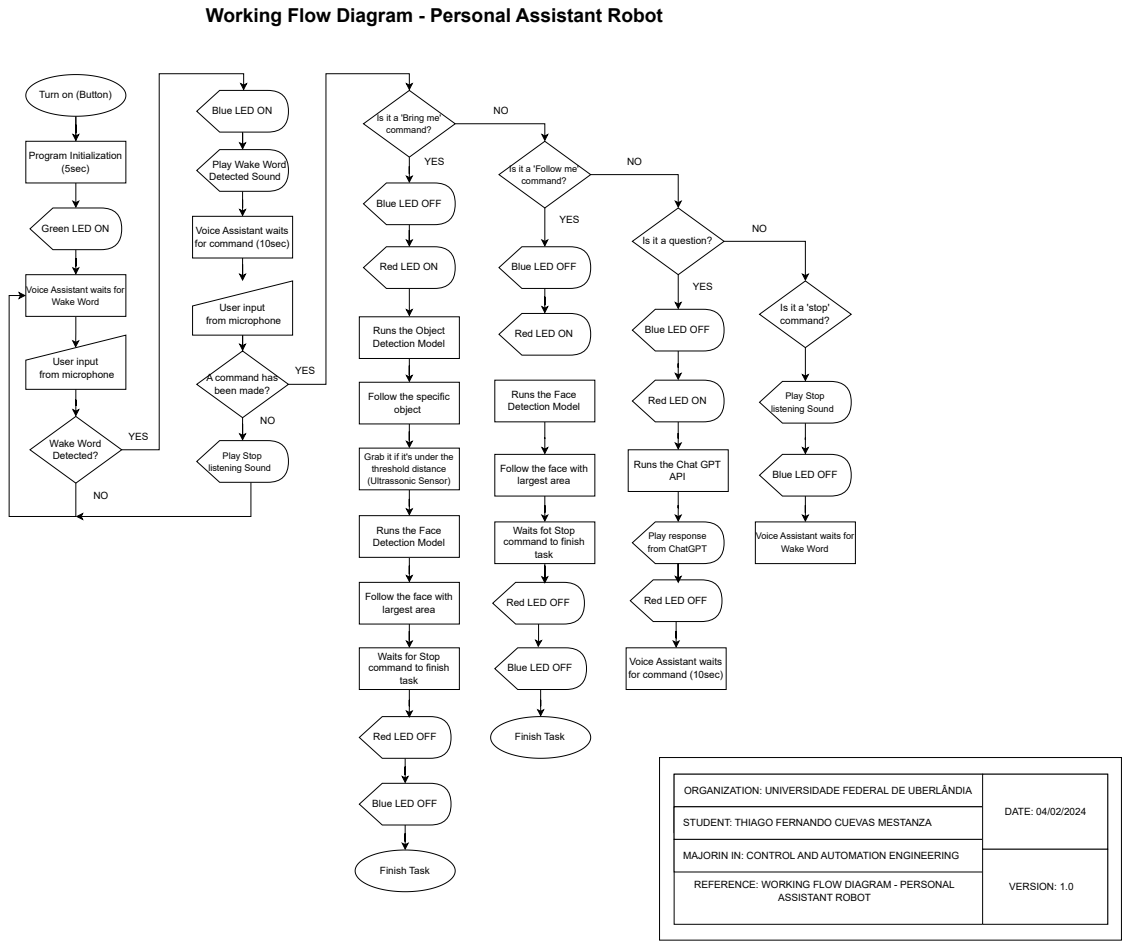
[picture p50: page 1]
Program Initialization (5sec); Wake Word Detected?; YES; A command has been made?; Play Stop listening Sound; User input from microphone; API; Red LED OFF; Play response from ChatGPT; Finish Task; ASSISTANT ROBOT; DATE: 04/02/2024; VERSION: 1.0

Turn on (Button)

Blue LED ON

Is it a 'Bring me'
command?

Play Wake Word
Detected Sound

Is it a 'Follow me'

Blue LED OFF

Green LED ON

Voice Assistant waits
for command (10sec)

Is it a question?

Red LED ON

Voice Assistant waits for

Wake Word

Is it a 'stop'

Runs the Object Detection Model

Follow the specific
object

Runs the Face
Detection Model

Grab it if it's under the
threshold distance
(Ultrassonic Sensor)

Runs the Chat GPT

Follow the face with
largest area

Waits fot Stop
command to finish
task

Waits for Stop

Red LED OFF

ORGANIZATION: UNIVERSIDADE FEDERAL DE UBERLÂNDIA

STUDENT: THIAGO FERNANDO CUEVAS MESTANZA

MAJORIN IN: CONTROL AND AUTOMATION ENGINEERING

REFERENCE: WORKING FLOW DIAGRAM - PERSONAL

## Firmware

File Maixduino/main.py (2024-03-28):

from Maix import GPIO
from fpioa_manager import fm
import sensor,lcd,image
import KPU as kpu
from machine import UART, PWM, Timer
import machine
import utime
import _thread
import ujson
import os
import time

#Define uart pins and configurations
fm.register(22, fm.fpioa.UART2_RX, force=True)
fm.register(23, fm.fpioa.UART2_TX, force=True)
fm.register(24, fm.fpioa.UART1_RX, force=True)
fm.register(32, fm.fpioa.UART1_TX, force=True)

uart = UART(UART.UART1, 115200, 8, None, 1, read_buf_len=4096)
uart_stm32 = UART(UART.UART2, 115200, 8, None, 1,  read_buf_len=4096)
timx = Timer(Timer.TIMER0, Timer.CHANNEL0, mode=Timer.MODE_PWM)
timy = Timer(Timer.TIMER0, Timer.CHANNEL1, mode=Timer.MODE_PWM)
S1 = PWM(timx, freq=50, duty=0, pin=14)
S2 = PWM(timy, freq=50, duty=0, pin=13)

uart_stop_message = '(00,00,00)'

#function to write an angle in the servo motor
def Servo(servo,angle):
    servo.duty((angle+90)/180*10+2.5)

#run the object recognition model
def object_recognition_task(target_object):

    #object detection setup
    classes = ['aeroplane', 'bicycle', 'bird', 'boat', 'bottle', 'bus', 'car', 'cat', 'chair', 'cow', 'diningtable', 'dog', 'horse', 'motorbike', 'person', 'pottedplant', 'sheep', 'sofa', 'train', 'tvmonitor']
    task = kpu.load(0x500000)
    anchor = (1.08, 1.19, 3.42, 4.41, 6.63, 11.38, 9.42, 5.11, 16.62, 10.52)
    a = kpu.init_yolo2(task, 0.7, 0.3, 5, anchor)

    lcd.init()
    #lcd.rotation(2)
    sensor.reset()
    sensor.set_pixformat(sensor.RGB565)
    sensor.set_framesize(sensor.QVGA) #(320x240)
    #sensor.set_vflip(1)
    sensor.run(1)
    clock = time.clock()

    #initialize the servo in position 0 degrees
    servo_angle_x = 0
    servo_angle_y = 0
    Servo(S1, servo_angle_x)
    Servo(S2, servo_angle_y)
    time.sleep(5)

    #create arrays of 80 positions
    rank_array = ([0 for x in range(80)])
    all_area   = ([0 for x in range(80)])
    location_x   = ([0 for x in range(80)])
    location_y   = ([0 for x in range(80)])


    while(True):
        #image capture
        clock.tick()
        img = sensor.snapshot()

        #object detection with yolo2
        objects = kpu.run_yolo2(task, img)

        # if objects are detected on camera by yolo:
        if objects:
            number_obj = 0
            count = 0
            id_area = 0

            for obj in objects:

                if classes[obj.classid()] == target_object:

                    img.draw_rectangle(obj.rect(),color=(0,255,0),thickness=3)
                    img.draw_string(obj.x(), obj.y(), classes[obj.classid()], color=(0,255,0),scale=2)
                    img.draw_string(obj.x(), obj.y()+12, '%.3f'%obj.value(), color=(0,255,0),scale=2) #confidence value

                    #calculates the center cordinate of the object (centroid_x, centroid_y)
                    centroid_x = int(obj.w() / 2)
                    centroid_y = int(obj.h() / 2)

                    #save the centroid coordinate of each object in a array containing all objects centroid coordinates
                    location_x[number_obj] = obj.x() + centroid_x
                    location_y[number_obj] = obj.y() + centroid_y

                    #save the area of each object in a array containing all objects areas
                    all_area[number_obj] = obj.w() * obj.h()
                    largest_obj_area = all_area[number_obj]
                    # print(largest_obj_area)

                    #increase the index for the next object
                    number_obj +=1

                    #draw a circle on the center of the object with largest area
                    a = img.draw_circle(location_x[id_area], location_y[id_area], 3, color=(255,0, 0), fill=True)

                    error_y = location_y[id_area] - 120 # 120 = (display length / 2) pixels

                    #print(error_y)
                    if error_y > 50:
                        servo_angle_y = servo_angle_y-2
                        if servo_angle_y < -90:
                            servo_angle_y = -90
                        Servo(S2,servo_angle_y)
                    if error_y < 30:
                        servo_angle_y = servo_angle_y+2
                        if servo_angle_y > 90:
                            servo_angle_y=90
                        Servo(S2,servo_angle_y)

                    #set the x limits of the display
                    display_x_min = 0
                    display_x_max = 320

                    #set the limits of the screen localization to the motors (10 - 99)
                    out_max_motor = 99
                    out_min_motor = 10

                    #set the limits of the object area
                    in_min_obj = 12000
                    in_max_obj = 60000
                    linear_obj_area = int((largest_obj_area - in_min_obj) * (out_max_motor - out_min_motor) / (in_max_obj - in_min_obj) + out_min_motor)

                    #set the coordinates to send to the stm32
                    obj_x_coordinate = int(((location_x[id_area] - display_x_min) * (out_max_motor - out_min_motor) / (display_x_max - display_x_min) + out_min_motor))
                    obj_y_coordinate = 10 #so pra teste

                    #print(location_x[id_area])
                    #print(obj_x_coordinate)

                    uart_coord_message = '(' + str(obj_x_coordinate) + ',' + str(obj_y_coordinate) + ',' + str(linear_obj_area) + ')'
                    uart_stm32.write(uart_coord_message)
                    #print(uart_coord_message)

                else:
                    #for each object detected the program will draw a rectangle around the object with his name and porcentage of confidence
                    img.draw_rectangle(obj.rect(),color=(255,0,0),thickness=3) #draw the rectangle
                    img.draw_string(obj.x(), obj.y(), classes[obj.classid()], color=(255,0,0),scale=2) #write the name of the object
                    img.draw_string(obj.x(), obj.y()+12, '%.3f'%obj.value(), color=(255,0,0),scale=2) #confidence value
                    name = classes[obj.classid()]  #get the name of the object


        else:
            uart_stm32.write(uart_stop_message)
            print("stop message")

        a = lcd.display(img) #refresh the display

        if uart.any():
            stop = uart.read()
            stop_decoded = stop.decode('utf-8')
            if stop_decoded == 'stop':
                kpu.deinit(task)
                lcd.clear()
                #uart.write(b'task-finish')
                #print('atividade finalizada')
                waiting_command()
        else:
            pass


def waiting_command():

    lcd.init()
    img = image.Image(size=(160, 120))
    img.draw_string(0,50, "waiting command", lcd.WHITE, lcd.BLACK, scale=2)
    lcd.display(img)

    while True:
        if uart.any():
            command = uart.read()
            command_decoded = command.decode('utf-8')
            if command_decoded == 'follow':
                print('mensagem follow recebida')
                follow_task()
            else:
                obj = command_decoded.split("-")
                #print(obj[1])
                if obj[0] == 'bring':
                    print('mensagem bring recebida!')
                    object_recognition_task(obj[1])


def follow_task():

    lcd.init()
    sensor.reset()
    sensor.set_pixformat(sensor.RGB565)
    sensor.set_framesize(sensor.QVGA)

    #lcd.mirror(True)
    clock = time.clock()

    rank_array = ([0 for x in range(80)])
    faces_areas   = ([0 for x in range(80)])
    face_location_x   = ([0 for x in range(80)])
    face_location_y   = ([0 for x in range(80)])

    servo_angle_x = 0
    servo_angle_y = 0
    Servo(S1, servo_angle_x)
    Servo(S2, servo_angle_y)

    task = kpu.load("/sd/facedetect.kmodel")

    #face detection setup
    anchor = (1.889, 2.5245, 2.9465, 3.94056, 3.99987, 5.3658, 5.155437, 6.92275, 6.718375, 9.01025)
    a = kpu.init_yolo2(task, 0.5, 0.3, 5, anchor)

    while(True):
        clock.tick()
        img = sensor.snapshot()
        faces = kpu.run_yolo2(task, img)
        largest_face_area = 0

        if faces:
            number_faces=0
            largest_face_area=0

            for face in faces:

                #for each face detected the program will draw a rectangle around
                b = img.draw_rectangle(face.rect(),color=(0,255,0), thickness=3) #draw a rectangles around face

                #for each face detected the program will write "face" and write the confidence value
                img.draw_string(face.x(), face.y(), "face",color=(0,255,0),scale=2) #write the name of the object
                img.draw_string(face.x(), face.y()+12, '%.3f'%face.value(), color=(0,255,0),scale=2) #confidence value

                #calculates the center cordinate of the object (centroid_x, centroid_y)
                face_centroid_x = int(face.w() / 2)
                face_centroid_y = int(face.h() / 2)

                #save the centroid coordinate of each object in a array containing all objects centroid coordinates
                face_location_x[number_faces] = face.x() + face_centroid_x
                face_location_y[number_faces] = face.y() + face_centroid_y

                #save the area of each object in a array containing all objects areas
                faces_areas[number_faces] = face.w() * face.h()

                #print('area  ')
                #print(faces_areas[number_faces])

                #increase the index for the next face
                number_faces +=1

            #finds out what is the face with largest area (the closest face) captured by the camera
            for i in range(len(faces_areas)):
                for j in range(number_faces):
                    #verify if the area of the object j has the bigger value on the rank_array to storage the largest area of all objects
                    if faces_areas[j] > largest_face_area:
                        largest_face_area = faces_areas[j] #save the largest area on the rank_array[0]
                        id_area = j  #save the id of the largest object
                        #print(faces_areas[j])

            a = img.draw_circle(face_location_x[id_area], face_location_y[id_area], 3, color=(255, 0, 0), fill=True) #draw a circle on the center of the object with largest area

            error_y = face_location_y[id_area] - 120 # 120 = (display length / 2) pixels

            #print(error_y)
            if error_y > 50:
                servo_angle_y = servo_angle_y-2
                if servo_angle_y < -90:
                    servo_angle_y = -90
                Servo(S2,servo_angle_y)
            if error_y < 30:
                servo_angle_y = servo_angle_y+2
                if servo_angle_y > 90:
                    servo_angle_y=90
                Servo(S2,servo_angle_y)


            #set the x limits of the display (0 -> 320)
            display_min = 0
            display_max = 320

            #set the limits of the screen localization to the motors (10 - 99)
            out_max_motor = 99
            out_min_motor = 10

            #set the limits of the face area
            in_min_face = 300
            in_max_face = 40000
            linear_face_area = int((largest_face_area - in_min_face) * (out_max_motor - out_min_motor) / (in_max_face - in_min_face) + out_min_motor)

            #storages the x porcentage in a variable
            coordinate_x_motor = int(((face_location_x[id_area] - display_min) * (out_max_motor - out_min_motor) / (display_max - display_min) + out_min_motor))
            coordinate_y_motor = 10 #so pra teste

            uart_coord_message = '(' + str(coordinate_x_motor) +',' + str(coordinate_y_motor) + ',' + str(linear_face_area) + ')'
            uart_stm32.write(uart_coord_message)
            print(uart_coord_message)
            print()

        else:
            uart_stm32.write(uart_stop_message)
            print("stop message")


        lcd.display(img)
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

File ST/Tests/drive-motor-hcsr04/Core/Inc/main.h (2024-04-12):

/* USER CODE BEGIN Header */
/**
  ******************************************************************************
  * @file           : main.h
  * @brief          : Header for main.c file.
  *                   This file contains the common defines of the application.
  ******************************************************************************
  * @attention
  *
  * Copyright (c) 2023 STMicroelectronics.
  * All rights reserved.
  *
  * This software is licensed under terms that can be found in the LICENSE file
  * in the root directory of this software component.
  * If no LICENSE file comes with this software, it is provided AS-IS.
  *
  ******************************************************************************
  */
/* USER CODE END Header */

/* Define to prevent recursive inclusion -------------------------------------*/
#ifndef __MAIN_H
#define __MAIN_H

#ifdef __cplusplus
extern "C" {
#endif

/* Includes ------------------------------------------------------------------*/
#include "stm32f4xx_hal.h"

/* Private includes ----------------------------------------------------------*/
/* USER CODE BEGIN Includes */

/* USER CODE END Includes */

/* Exported types ------------------------------------------------------------*/
/* USER CODE BEGIN ET */

/* USER CODE END ET */

/* Exported constants --------------------------------------------------------*/
/* USER CODE BEGIN EC */

/* USER CODE END EC */

/* Exported macro ------------------------------------------------------------*/
/* USER CODE BEGIN EM */
//void readbuffer(struct Coordinate* coord);

//double pid_control (int x, int y);
/* USER CODE END EM */

void HAL_TIM_MspPostInit(TIM_HandleTypeDef *htim);

/* Exported functions prototypes ---------------------------------------------*/
void Error_Handler(void);

/* USER CODE BEGIN EFP */
void motor_handle(int x, int area, uint16_t stop_flag);

void HAL_TIM_IC_CaptureCallback(TIM_HandleTypeDef *htim);
/* USER CODE END EFP */

/* Private defines -----------------------------------------------------------*/
#define TIM5_CH1_Pin GPIO_PIN_0
#define TIM5_CH1_GPIO_Port GPIOA
#define GREEN_LED_Pin GPIO_PIN_13
#define GREEN_LED_GPIO_Port GPIOB
#define RED_LED_Pin GPIO_PIN_14
#define RED_LED_GPIO_Port GPIOB

/* USER CODE BEGIN Private defines */

/* USER CODE END Private defines */

#ifdef __cplusplus
}
#endif

#endif /* __MAIN_H */

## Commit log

2023-08-15 teste update 13.1v stmcubeide on bestpc
2023-08-15 sensor not responding
2023-08-16 sensor and led working
2023-08-16 led and sensor working?
2023-08-16 led and sensor working all right
2023-08-16 ultrassonic sensor and motor running with 2 detours bug
2023-08-26 motor and sensor running ok with new pcb
2023-08-26 motor.c updated
2023-08-26 motor.c updated v2
2023-08-26 teste on motor.c
2023-08-26 ultrassonic sensor and motors working fine
2024-01-30 Serial communication between maix and stm32
2024-02-03 Motors following object/face
2024-02-03 motor-tracking-objects gif added
2024-02-07 Buzzer and Leds added
2024-02-28 PCB Files and 3D images added
2024-02-28 PCB Images added
2024-03-21 PCB and 3DStructure done
2024-04-12 stl files added
    [1st-Half-Hook-Support.stl, 2nd-Half-Hook-Support.stl, Base-Hook-Support.stl, Base-Motor-Hook.stl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]
